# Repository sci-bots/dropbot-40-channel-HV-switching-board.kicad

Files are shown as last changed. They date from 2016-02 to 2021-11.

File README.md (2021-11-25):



# DropBot v3 40-channel high-voltage switching board

The high-voltage switching boards control the on/off state of electrodes in the [DropBot system][dropbot]. Each board controls 40-channels and multiple boards can be daisy-chained together.

For more information, please visit https://sci-bots.com

[Sci-Bots logo][sci-bots]

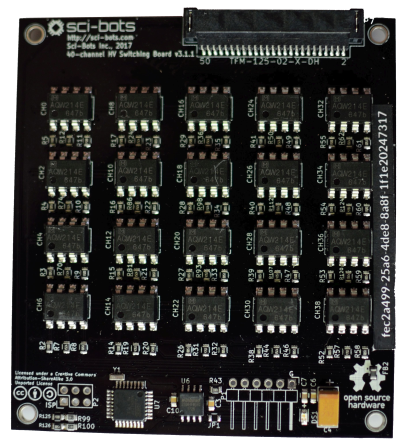
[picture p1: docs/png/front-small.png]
front

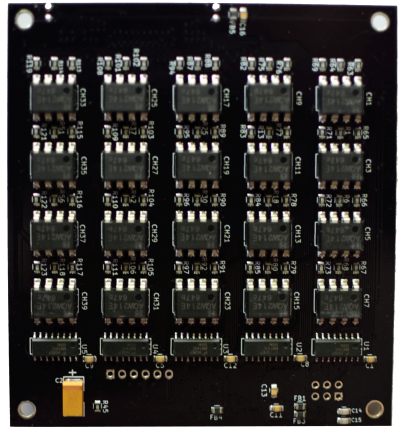
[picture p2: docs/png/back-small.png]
back


This design is open-source hardware released under a [Creative Commons Attribution-ShareAlike licence][cc-by-sa].

[][cc-by-sa]

[dropbot]: https://github.com/sci-bots/dropbot-v3
[sci-bots]: https://sci-bots.com/
[cc-by-sa]: http://creativecommons.org/licenses/by-sa/3.0

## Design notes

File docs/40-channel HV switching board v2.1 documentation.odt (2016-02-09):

40-channel HV switching board v2.1

http://microfluidics.utoronto.ca/trac/dropbot/wiki/HighVoltageSwitchingBoard

Document revision: 1

Last updated: 2016-02-09

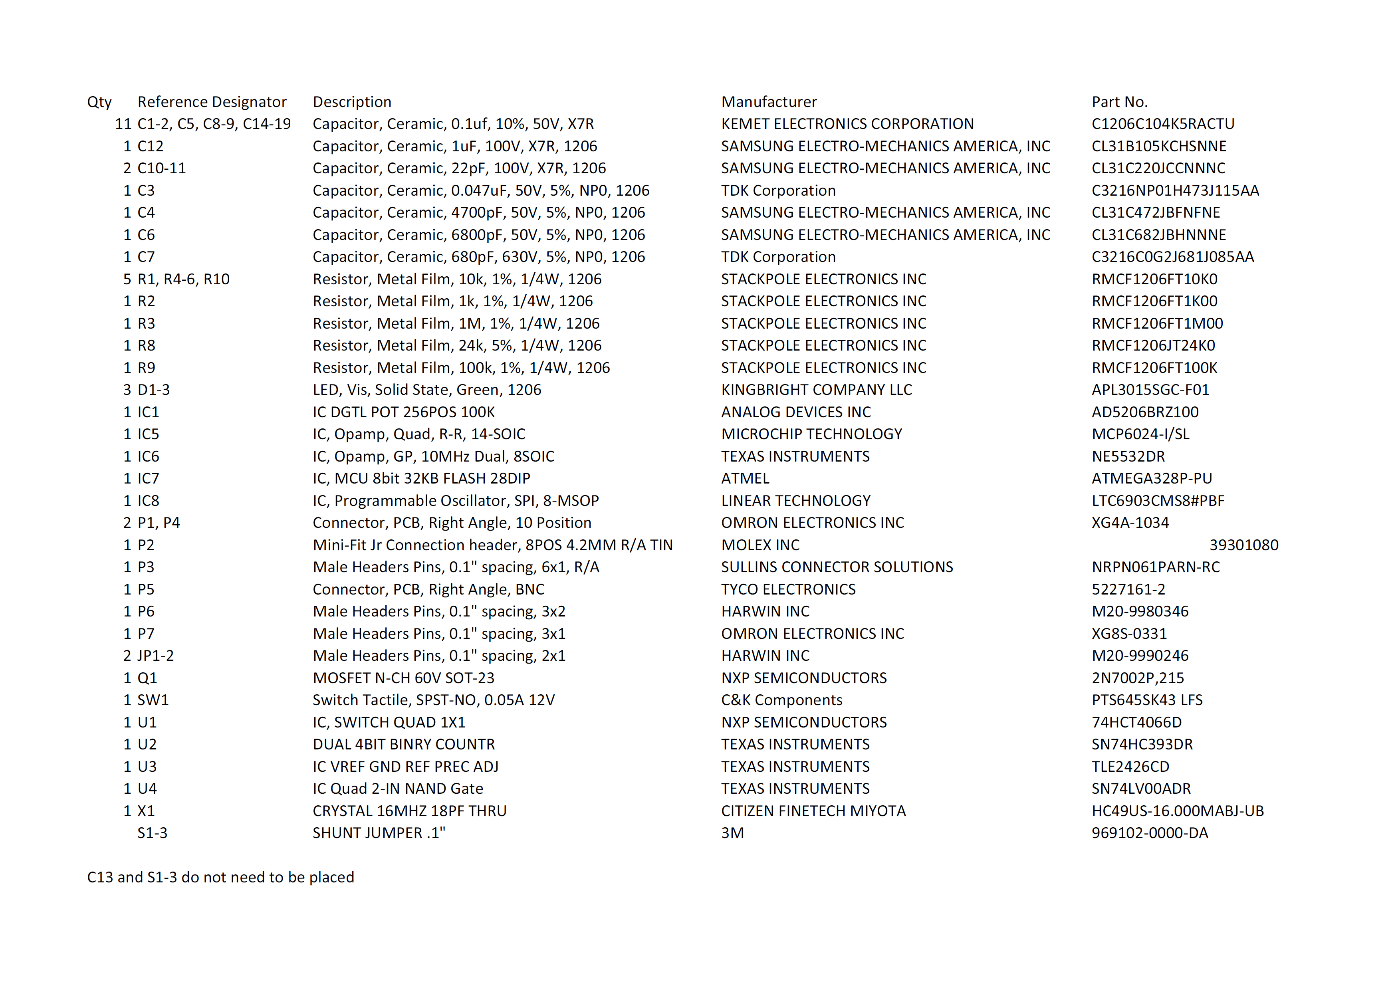
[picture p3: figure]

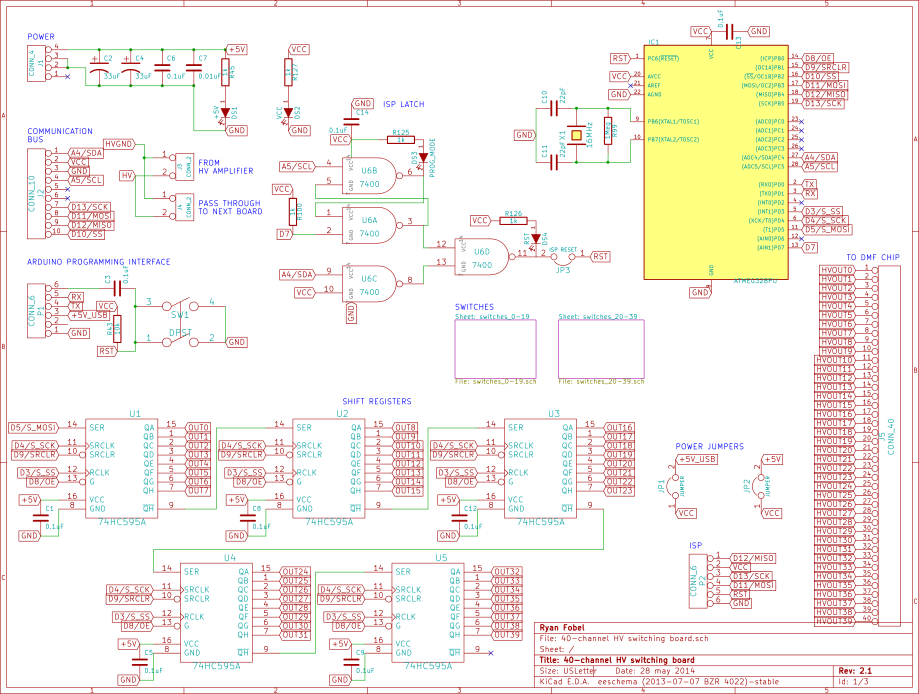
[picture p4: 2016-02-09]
docs/png/40-channel HV switching board schematic p1.png

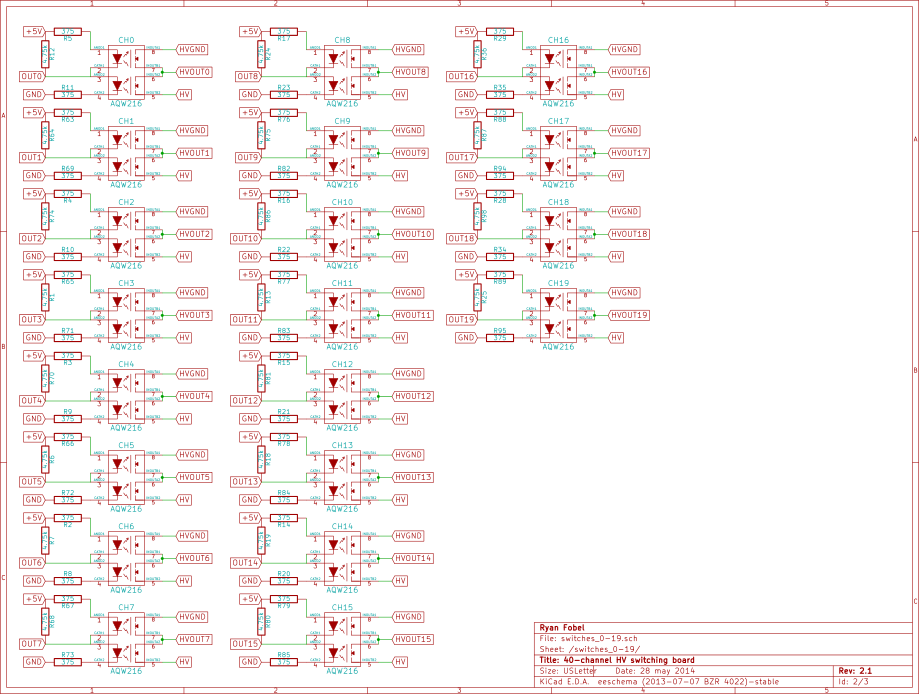
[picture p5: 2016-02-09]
docs/png/40-channel HV switching board schematic p2.png

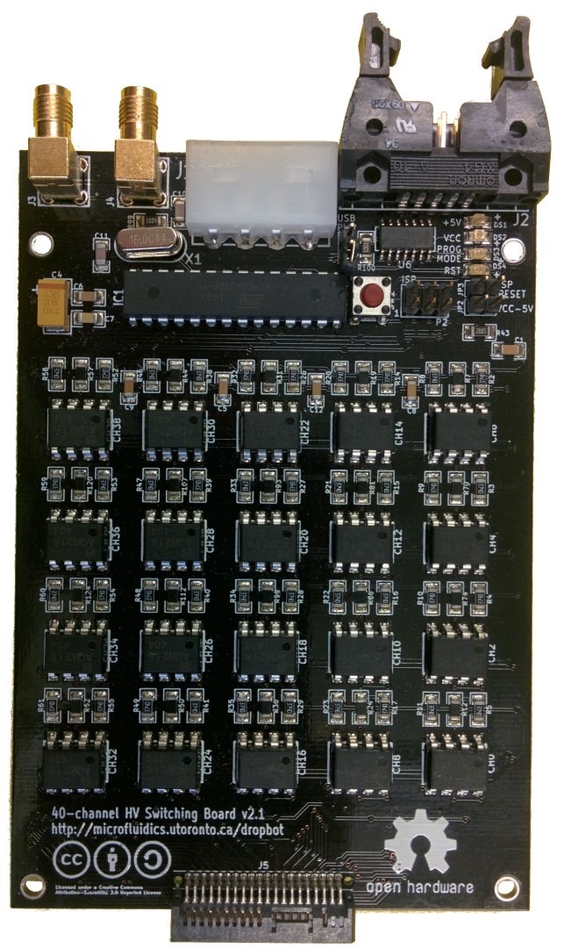
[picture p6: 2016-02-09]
docs/src/HV_Switching_Board_v2.1(front).jpg

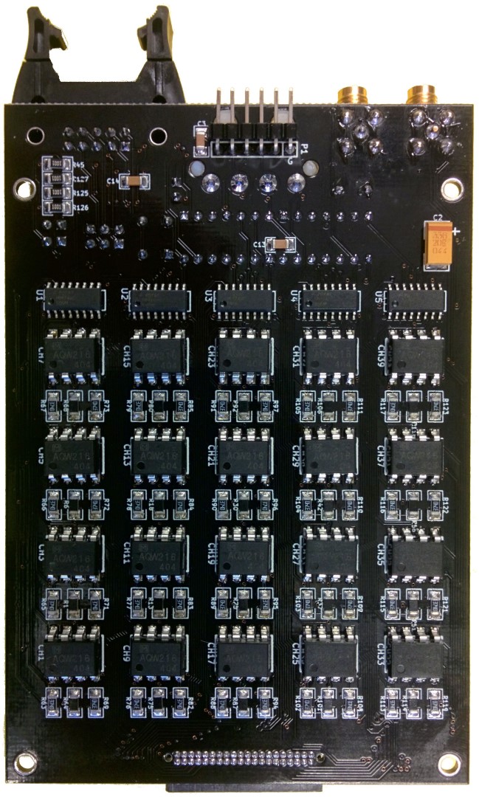
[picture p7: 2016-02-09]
docs/src/HV_Switching_Board_v2.1(back).jpg

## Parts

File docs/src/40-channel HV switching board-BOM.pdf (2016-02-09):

Item # | Qty Reference Designator | Description | Package Manufacturer | Part No. | Digikey Part No.
1 | 2 C10 C11 | Capacitor, Ceramic, 22pF, 100V, X7R, 1206 | 1206 SAMSUNG ELECTRO-MECHANICS AMERICA, INC | CL31C220JCCNNNC | 1276-2820-1-ND
2 | 1 C7 | Capacitor, Ceramic, 0.01uf, 10%, 50V, X7R | 1206 SAMSUNG ELECTRO-MECHANICS AMERICA, INC | CL31B103KBCNNNC | 1276-1035-1-ND
3 | 9 C1 C3 C5 C6 C8 C9 C12 C13 C14 | Capacitor, Ceramic, 0.1uf, 10%, 50V, X7R | 1206 KEMET ELECTRONICS CORPORATION | C1206C104K5RACTU | 399-1249-1-ND
4 | 2 C2 C4 | Capacitor, Tantalum, 33uf, 10%, 20V | 1206 KEMET ELECTRONICS CORPORATION | T491D336K020AT | 399-3788-1-ND

5 40

CH0 CH1 CH2 CH3 CH4 CH5 CH6 CH7 CH8 CH9
CH10 CH11 CH12 CH13 CH14 CH15 CH16 CH17
CH18 CH19 CH20 CH21 CH22 CH23 CH24 CH25
CH26 CH27 CH28 CH29 CH30 CH31 CH32 CH33
| CH34 CH35 CH36 CH37 CH38 CH39 | Relay, PhotoMOS, 600V | 8-SMD | Panasonic Electric Works | AQW216A | 255-1969-ND
6 | 4 DS1 DS2 DS3 DS4 | LED, Vis, Solid State, Green | 1206 KINGBRIGHT COMPANY LLC | APL3015SGC-F01 | 754-1111-1-ND
7 | 1 IC1 | IC, MCU 8bit 32KB FLASH 28DIP | 28DIP | ATMEL | ATMEGA328P-PU | ATMEGA328P-PU-ND
8 | 1 J1 | Connnection Header, 4 Position, .200, RT ANG | header | Molex Inc | 15-24-4441 | WM6988-ND
9 | 1 J2 | Connector, PCB, Right Angle, 10 Position | header | OMRON ELECTRONICS INC | XG4A-1034 | OR1001-ND
10 | 2 J3 J4 | Connector, PCB, Right Angle, SMA | header | TE CONNECTIVITY | 5-1814400-1 | A97593-ND
11 | 1 J5 | Connector, 0.05", Right Angle Header, 40 Position | header | Samtec Inc | TFML-120-01-S-D-RA | SAM8266-ND
12 | 3 JP1 JP2 JP3 | Male Headers Pins, 0.1" spacing, 2x1 | header | Harwin Inc | M20-9990246 | 952-2121-ND
13 | 1 P1 | Male Headers Pins, 0.1" spacing, 6x1, R/A | header | SULLINS CONNECTOR SOLUTIONS | PRPC006SBAN-M71RC | S1111EC-06-ND
14 | 1 P2 | Male Headers Pins, 0.1" spacing, 3x2 | header | HARWIN INC | M20-9980346 | 952-2121-ND

15 80

R2 R3 R4 R5 R8 R9 R10 R11 R14 R15 R16 R17
R20 R21 R22 R23 R26 R27 R28 R29 R32 R33 R34
R35 R38 R39 R40 R41 R46 R47 R48 R49 R52 R53 R54 R55 R58 R59 R60 R61 R63 R65 R66 R67 R69 R71 R72 R73 R76 R77 R78 R79 R82 R83 R84 R85
R88 R89 R90 R91 R94 R95 R96 R97 R102 R103
R104 R105 R108 R109 R110 R111 R113 R115
| R116 R117 R119 R121 R122 R123 | Resistor, Metal Film, 374, 1%, 1/4W | 1206 Yageo | RC1206FR-07374RL | 311-374FRCT-ND
16 | 4 R45 R100 R125 R126 R127 | Resistor, Metal Film, 1k, 1%, 1/4W, 1206 | 1206 STACKPOLE ELECTRONICS INC | RMCF1206FT1K00 | RMCF1206FT1K00CT-ND

17 40

R1 R6 R7 R12 R13 R18 R19 R24 R25 R30 R31
R36 R37 R42 R44 R50 R51 R56 R57 R62 R64 R68
R70 R74 R75 R80 R81 R86 R87 R92 R93 R98
R101 R106 R107 R112 R114 R118 R120 R124 | Resistor, Metal Film, 4.75k, 1%, 1/8W | 1206 Yageo | RC1206FR-074K75L | 311-4.75KFRCT-ND
18 | 1 R43 | Resistor, Metal Film, 10k, 1%, 1/4W, 1206 | 1206 STACKPOLE ELECTRONICS INC | RMCF1206FT10K0 | RMCF1206FT10K0TR-ND
19 | 1 R99 | Resistor, Metal Film, 1M, 1%, 1/4W, 1206 | 1206 STACKPOLE ELECTRONICS INC | RMCF1206FT1M00 | RMCF1206FT1M00TR-ND
20 | 3 S1 S2 S3 | Shunt Jumper .1" | N/A | 3M | 969102-0000-DA | 3M9580-ND
21 | 1 SW1 | Switch Tactile, SPST-NO, 0.05A 12V | button | C&K Components | PTS645SK43 LFS | CKN9090-ND
22 | 1 U6 | IC Quad 2-IN NAND Gate | 14-SOIC Texas Instruments | SN74LV00ADR | 296-1670-1-ND
23 | 5 U1 U2 U3 U4 U5 | IC Shift Register 8-BIT | 16-SOIC Fairchild Semiconductor | MM74HC595MX | MM74HC595MXCT-ND
24 | 1 X1 | Crytal 16MHZ 18pF | HC49/US CITIZEN FINETECH MIYOTA | HC49US-16.000MABJ-UB 300-8499-ND

Note: S1-3 do not need to be placed

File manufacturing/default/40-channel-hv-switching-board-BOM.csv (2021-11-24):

Refs | Quantity | MPN | Manufacturer | datasheet | footprint | value
C1, C3, C5, C6, C8-C13, C16 | 11 | CL21B104KBCNNNC | Samsung |  | Capacitors_SMD:C_0805 | 0.1uF
C14, C15 | 2 | CL21C151JBANNNC | Samsung |  | Capacitors_SMD:C_0805 | 150pF
C2, C4 | 2 | T491D336K020AT | KEMET |  | Sci-Bots:SM2917 | 33uF
C7 | 1 | CL21B103KCANNNC | Samsung |  | Capacitors_SMD:C_0805 | 0.01uF
DS1 | 1 | 150080BS75000 | Würth Elektronik |  | LEDs:LED_0805 | +3.3V_PWR
FB1-FB5 | 5 | 742792040 | Würth Elektronik |  | Resistors_SMD:R_0805 | FERRITE
JP1 | 1 | DNP | DNP |  | Resistors_SMD:R_0805 | JUMPER
P1 | 1 | DNP | DNP |  | Pin_Headers:Pin_Header_Angled_1x06 | CONN_01X06
P2 | 1 | DNP | DNP |  | Pin_Headers:Pin_Header_Straight_2x03 | CONN_01X06
P3-P6 | 4 | DNP | DNP |  | Connect:1pin | CONN_01X01
P7 | 1 | TFM-125-02-L-DH | Samtec |  | Sci-Bots:TFM-125-02-X-DH | TFM-125-02-X-DH
R99, R100 | 2 | RC0805FR-0751RL | Yageo |  | Resistors_SMD:R_0805 | 51
R125, R126 | 2 | RC0805FR-07150RL | Yageo |  | Resistors_SMD:R_0805 | 150
R43 | 1 | RC0805FR-0710KL | Yageo |  | Resistors_SMD:R_0805 | 10k
R45 | 1 | RC0805FR-071KL | Yageo |  | Resistors_SMD:R_0805 | 1k
U1-U5 | 5 | MM74HC595MX | onsemi | ~ | Sci-Bots:SO16E | 74HC595A
U6 | 1 | W25Q64FVSSIG TR | Winbond |  | SMD_Packages:SOIC-8-N | W25Q64FV
U7 | 1 | ATMEGA328P-AU | Microchip |  | Housings_QFP:TQFP-32_7x7mm_Pitch0.8mm | ATMEGA328P-AU
Y1 | 1 | CSTCE8M00G55-R0 | Murata | http://www.murata.com/~/media/webrenewal/support/library/catalog/products/timingdevice/ceralock/p16e.ashx | Sci-Bots:CSTCE_G15C | RESONATOR
CH0-CH39 | 40 | AQW214EAZ | Panasonic |  | SMD_Packages:DIP-8_SMD | AQW214
R1, R6, R7, R12, R13, R18, R19, R24, R25, R30, R31, R36, R37, R42, R44, R50, R51, R56, R57, R62, R64, R68, R70, R74, R75, R80, R81, R86, R87, R92, R93, R98, R101, R106, R107, R112, R114, R118, R120, R124 | 40 | RC0805FR-074K75L | Yageo |  | Resistors_SMD:R_0805 | 4.75k
R2-R5, R8-R11, R14-R17, R20-R23, R26-R29, R32-R35, R38-R41, R46-R49, R52-R55, R58-R61, R63, R65-R67, R69, R71-R73, R76-R79, R82-R85, R88-R91, R94-R97, R102-R105, R108-R111, R113, R115-R117, R119, R121-R123 | 80 | RC0805FR-07220RL | Yageo |  | Resistors_SMD:R_0805 | 220

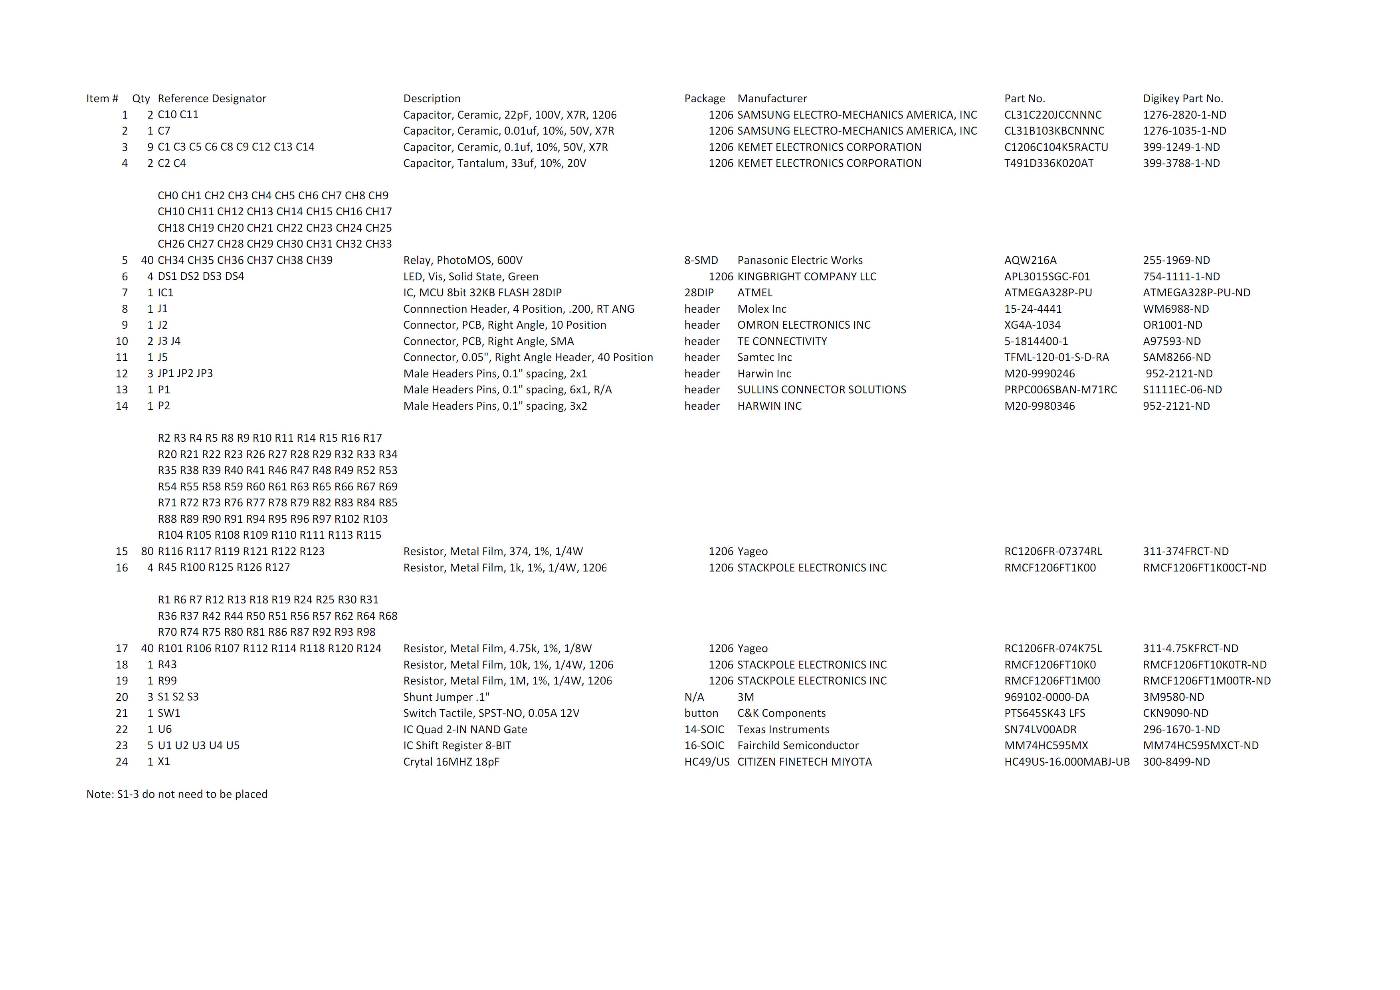
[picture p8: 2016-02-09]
docs/png/40-channel HV switching board-BOM.png

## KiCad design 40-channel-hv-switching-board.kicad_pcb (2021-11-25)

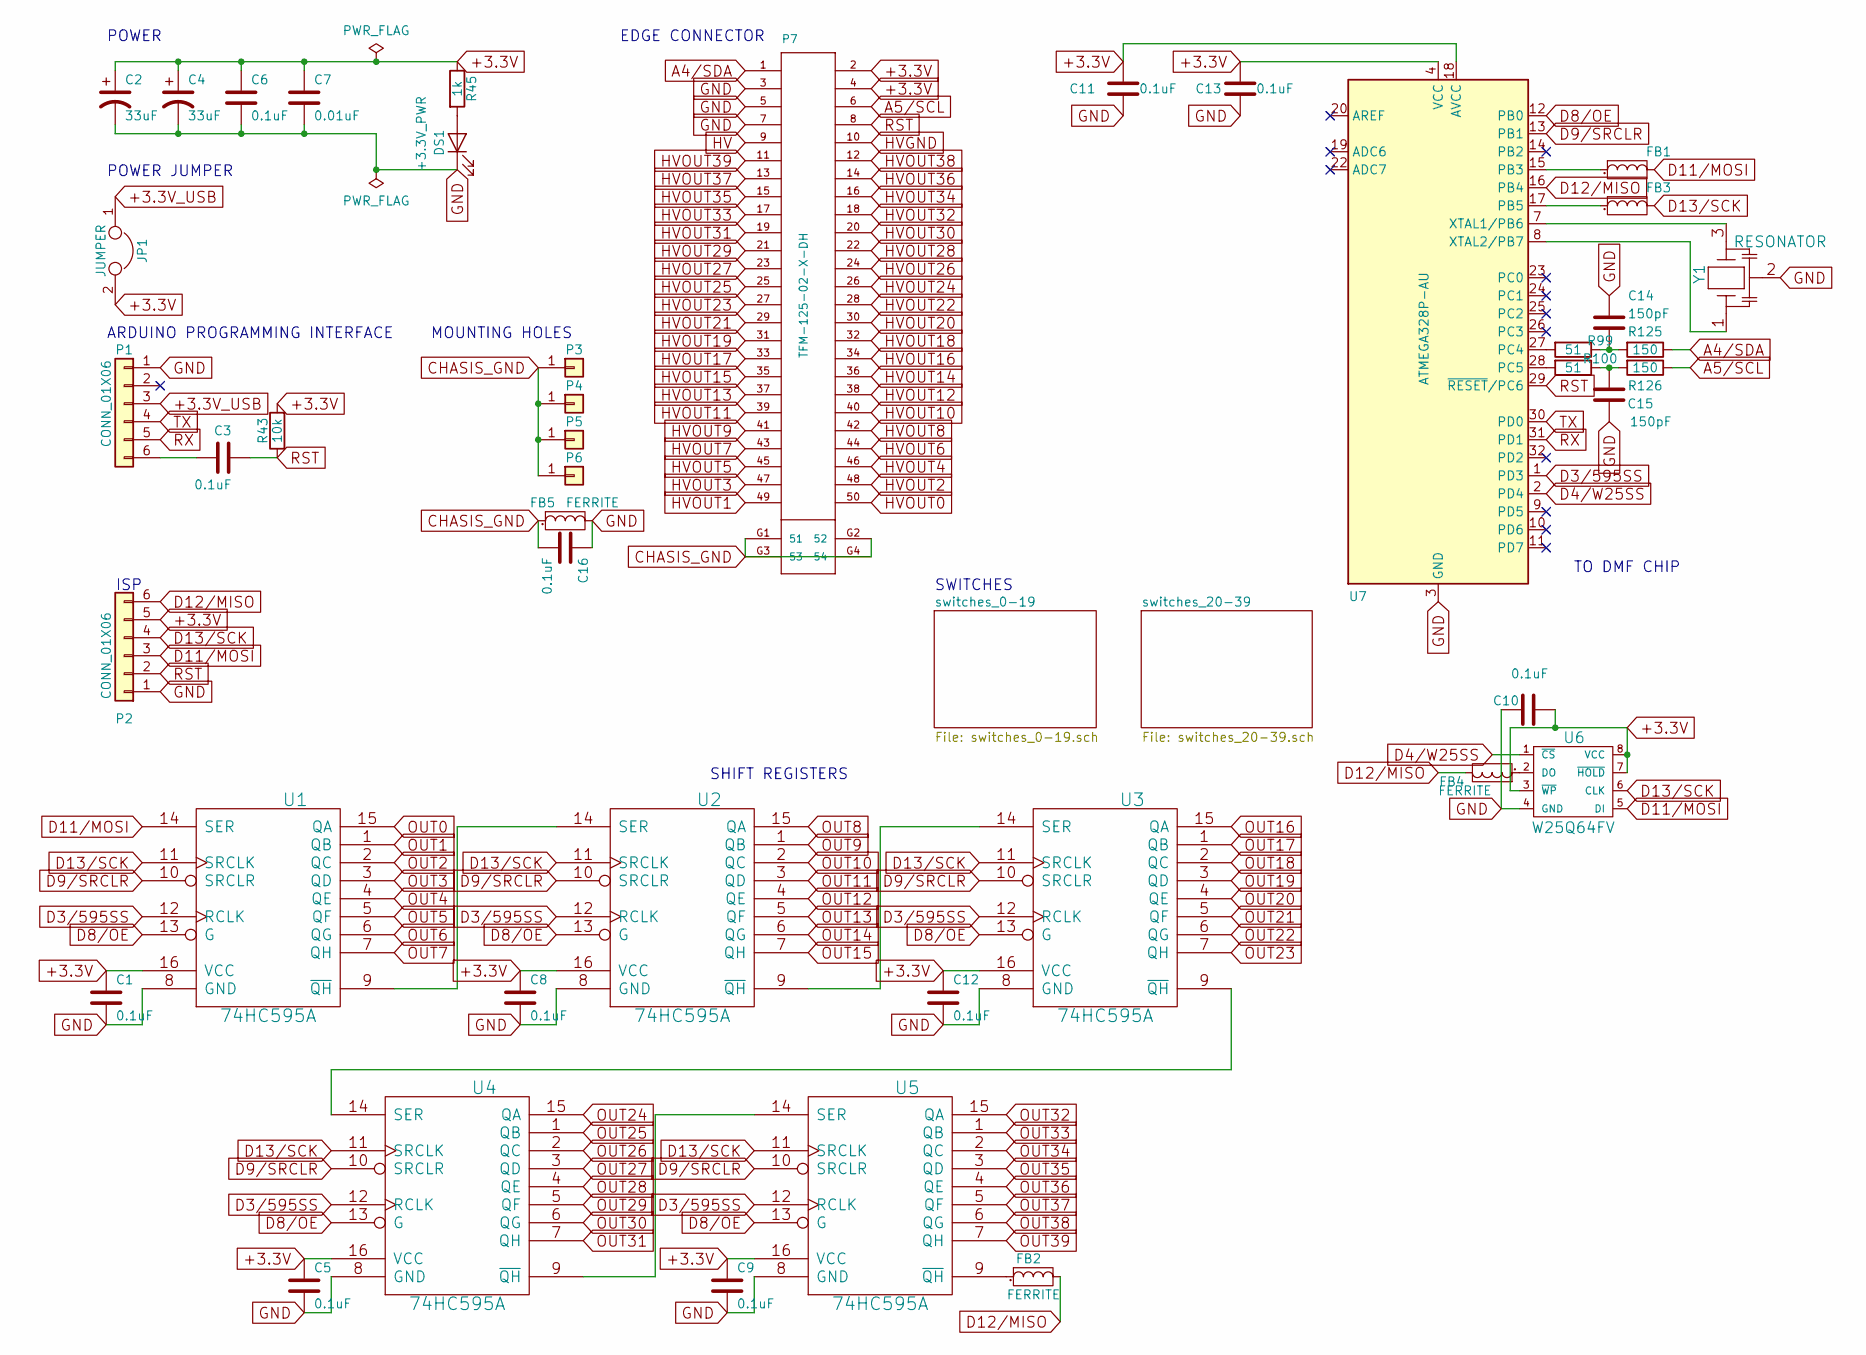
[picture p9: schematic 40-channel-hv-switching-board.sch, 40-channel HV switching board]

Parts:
C1, C3, C5, C6, C8, C9, C10, C11, C12, C13, C16: 0.1uF; C_0805; MPN CL21B104KBCNNNC
C2, C4: 33uF; SM2917; MPN T491D336K020AT
C7: 0.01uF; C_0805; MPN CL21B103KCANNNC
C14, C15: 150pF; C_0805; MPN CL21C151JBANNNC
DS1: +3.3V_PWR; LED_0805; MPN 150080BS75000
FB1, FB2, FB3, FB4, FB5: FERRITE; R_0805; MPN 742792040
JP1: JUMPER; R_0805; MPN DNP
P1: CONN_01X06; Pin_Header_Angled_1x06; MPN DNP
P2: CONN_01X06; Pin_Header_Straight_2x03; MPN DNP
P3, P4, P5, P6: CONN_01X01; 1pin; MPN DNP
P7: TFM-125-02-X-DH; MPN TFM-125-02-L-DH
R43: 10k; R_0805; MPN RC0805FR-0710KL
R45: 1k; R_0805; MPN RC0805FR-071KL
R99, R100: 51; R_0805; MPN RC0805FR-0751RL
R125, R126: 150; R_0805; MPN RC0805FR-07150RL
U1, U2, U3, U4, U5: 74HC595A; SO16E; MPN MM74HC595MX
U6: W25Q64FV; SOIC-8-N; MPN W25Q64FVSSIG TR
U7: ATMEGA328P-AU; TQFP-32_7x7mm_Pitch0.8mm; MPN ATMEGA328P-AU
Y1: RESONATOR; CSTCE_G15C; MPN CSTCE8M00G55-R0

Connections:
+3.3V: C1.1, C2.1, C4.1, C5.1, C6.1, C7.1, C8.1, C9.1, C10.1, C11.2, C12.1, C13.2, JP1.2, P2.5, P7.2, P7.4, R43.2, R45.1, U1.16 (VCC), U2.16 (VCC), U3.16 (VCC), U4.16 (VCC), U5.16 (VCC), U6.3 (~WP), U6.7 (~HOLD), U6.8 (VCC), U7.4 (VCC), U7.6 (VCC), U7.18 (AVCC); also elsewhere on the board
+3.3V_USB: JP1.1, P1.3
A4/SDA: P7.1, R125.1
A5/SCL: P7.6, R126.1
CHASIS_GND: C16.2, FB5.1, P3.1, P4.1, P5.1, P6.1, P7.G1 (51), P7.G2 (52), P7.G3 (53), P7.G4 (54)
D3/595SS: U1.12 (RCLK), U2.12 (RCLK), U3.12 (RCLK), U4.12 (RCLK), U5.12 (RCLK), U7.1 (PD3)
D4/W25SS: U6.1 (~CS), U7.2 (PD4)
D8/OE: U1.13 (G), U2.13 (G), U3.13 (G), U4.13 (G), U5.13 (G), U7.12 (PB0)
D9/SRCLR: U1.10 (SRCLR), U2.10 (SRCLR), U3.10 (SRCLR), U4.10 (SRCLR), U5.10 (SRCLR), U7.13 (PB1)
D11/MOSI: FB1.2, P2.3, U1.14 (SER), U6.5 (DI)
D12/MISO: FB2.2, FB4.2, P2.6, U7.16 (PB4)
D13/SCK: FB3.2, P2.4, U1.11 (SRCLK), U2.11 (SRCLK), U3.11 (SRCLK), U4.11 (SRCLK), U5.11 (SRCLK), U6.6 (CLK)
GND: C1.2, C2.2, C4.2, C5.2, C6.2, C7.2, C8.2, C9.2, C10.2, C11.1, C12.2, C13.1, C14.1, C15.1, C16.1, DS1.1 (K), FB5.2, P1.1, P2.1, P7.3, P7.5, P7.7, U1.8 (GND), U2.8 (GND), U3.8 (GND), U4.8 (GND), U5.8 (GND), U6.4 (GND), U7.3 (GND), U7.5 (GND), U7.21 (GND), Y1.2; also elsewhere on the board
HV: P7.9; also elsewhere on the board
HVGND: P7.10; also elsewhere on the board
HVOUT0: P7.50; also elsewhere on the board
HVOUT1: P7.49; also elsewhere on the board
HVOUT2: P7.48; also elsewhere on the board
HVOUT3: P7.47; also elsewhere on the board
HVOUT4: P7.46; also elsewhere on the board
HVOUT5: P7.45; also elsewhere on the board
HVOUT6: P7.44; also elsewhere on the board
HVOUT7: P7.43; also elsewhere on the board
HVOUT8: P7.42; also elsewhere on the board
HVOUT9: P7.41; also elsewhere on the board
HVOUT10: P7.40; also elsewhere on the board
HVOUT11: P7.39; also elsewhere on the board
HVOUT12: P7.38; also elsewhere on the board
HVOUT13: P7.37; also elsewhere on the board
HVOUT14: P7.36; also elsewhere on the board
HVOUT15: P7.35; also elsewhere on the board
HVOUT16: P7.34; also elsewhere on the board
HVOUT17: P7.33; also elsewhere on the board
HVOUT18: P7.32; also elsewhere on the board
HVOUT19: P7.31; also elsewhere on the board
HVOUT20: P7.30; also elsewhere on the board
HVOUT21: P7.29; also elsewhere on the board
HVOUT22: P7.28; also elsewhere on the board
HVOUT23: P7.27; also elsewhere on the board
HVOUT24: P7.26; also elsewhere on the board
HVOUT25: P7.25; also elsewhere on the board
HVOUT26: P7.24; also elsewhere on the board
HVOUT27: P7.23; also elsewhere on the board
HVOUT28: P7.22; also elsewhere on the board
HVOUT29: P7.21; also elsewhere on the board
HVOUT30: P7.20; also elsewhere on the board
HVOUT31: P7.19; also elsewhere on the board
HVOUT32: P7.18; also elsewhere on the board
HVOUT33: P7.17; also elsewhere on the board
HVOUT34: P7.16; also elsewhere on the board
HVOUT35: P7.15; also elsewhere on the board
HVOUT36: P7.14; also elsewhere on the board
HVOUT37: P7.13; also elsewhere on the board
HVOUT38: P7.12; also elsewhere on the board
HVOUT39: P7.11; also elsewhere on the board
unnamed: C3.1, P1.6
unnamed: C14.2, R99.1, R125.2
unnamed: C15.2, R100.1, R126.2
unnamed: DS1.2 (A), R45.2
unnamed: FB1.1, U7.15 (PB3)
unnamed: FB2.1, U5.9 (~QH)
unnamed: FB3.1, U7.17 (PB5)
unnamed: FB4.1, U6.2 (DO)
unnamed: R99.2, U7.27 (PC4)
unnamed: R100.2, U7.28 (PC5)
unnamed: U1.9 (~QH), U2.14 (SER)
unnamed: U2.9 (~QH), U3.14 (SER)
unnamed: U3.9 (~QH), U4.14 (SER)
unnamed: U4.9 (~QH), U5.14 (SER)
unnamed: U7.7 (XTAL1/PB6), Y1.3
unnamed: U7.8 (XTAL2/PB7), Y1.1
OUT0: U1.15 (QA); also elsewhere on the board
OUT1: U1.1 (QB); also elsewhere on the board
OUT2: U1.2 (QC); also elsewhere on the board
OUT3: U1.3 (QD); also elsewhere on the board
OUT4: U1.4 (QE); also elsewhere on the board
OUT5: U1.5 (QF); also elsewhere on the board
OUT6: U1.6 (QG); also elsewhere on the board
OUT7: U1.7 (QH); also elsewhere on the board
OUT8: U2.15 (QA); also elsewhere on the board
OUT9: U2.1 (QB); also elsewhere on the board
OUT10: U2.2 (QC); also elsewhere on the board
OUT11: U2.3 (QD); also elsewhere on the board
OUT12: U2.4 (QE); also elsewhere on the board
OUT13: U2.5 (QF); also elsewhere on the board
OUT14: U2.6 (QG); also elsewhere on the board
OUT15: U2.7 (QH); also elsewhere on the board
OUT16: U3.15 (QA); also elsewhere on the board
OUT17: U3.1 (QB); also elsewhere on the board
OUT18: U3.2 (QC); also elsewhere on the board
OUT19: U3.3 (QD); also elsewhere on the board
OUT20: U3.4 (QE); also elsewhere on the board
OUT21: U3.5 (QF); also elsewhere on the board
OUT22: U3.6 (QG); also elsewhere on the board
OUT23: U3.7 (QH); also elsewhere on the board
OUT24: U4.15 (QA); also elsewhere on the board
OUT25: U4.1 (QB); also elsewhere on the board
OUT26: U4.2 (QC); also elsewhere on the board
OUT27: U4.3 (QD); also elsewhere on the board
OUT28: U4.4 (QE); also elsewhere on the board
OUT29: U4.5 (QF); also elsewhere on the board
OUT30: U4.6 (QG); also elsewhere on the board
OUT31: U4.7 (QH); also elsewhere on the board
OUT32: U5.15 (QA); also elsewhere on the board
OUT33: U5.1 (QB); also elsewhere on the board
OUT34: U5.2 (QC); also elsewhere on the board
OUT35: U5.3 (QD); also elsewhere on the board
OUT36: U5.4 (QE); also elsewhere on the board
OUT37: U5.5 (QF); also elsewhere on the board
OUT38: U5.6 (QG); also elsewhere on the board
OUT39: U5.7 (QH); also elsewhere on the board
RST: C3.2, P2.2, P7.8, R43.1, U7.29 (~RESET~/PC6)
RX: P1.5, U7.31 (PD1)
TX: P1.4, U7.30 (PD0)

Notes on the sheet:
SHIFT REGISTERS
TO DMF CHIP
POWER
ARDUINO PROGRAMMING INTERFACE
ISP
POWER JUMPER
SWITCHES
EDGE CONNECTOR
MOUNTING HOLES

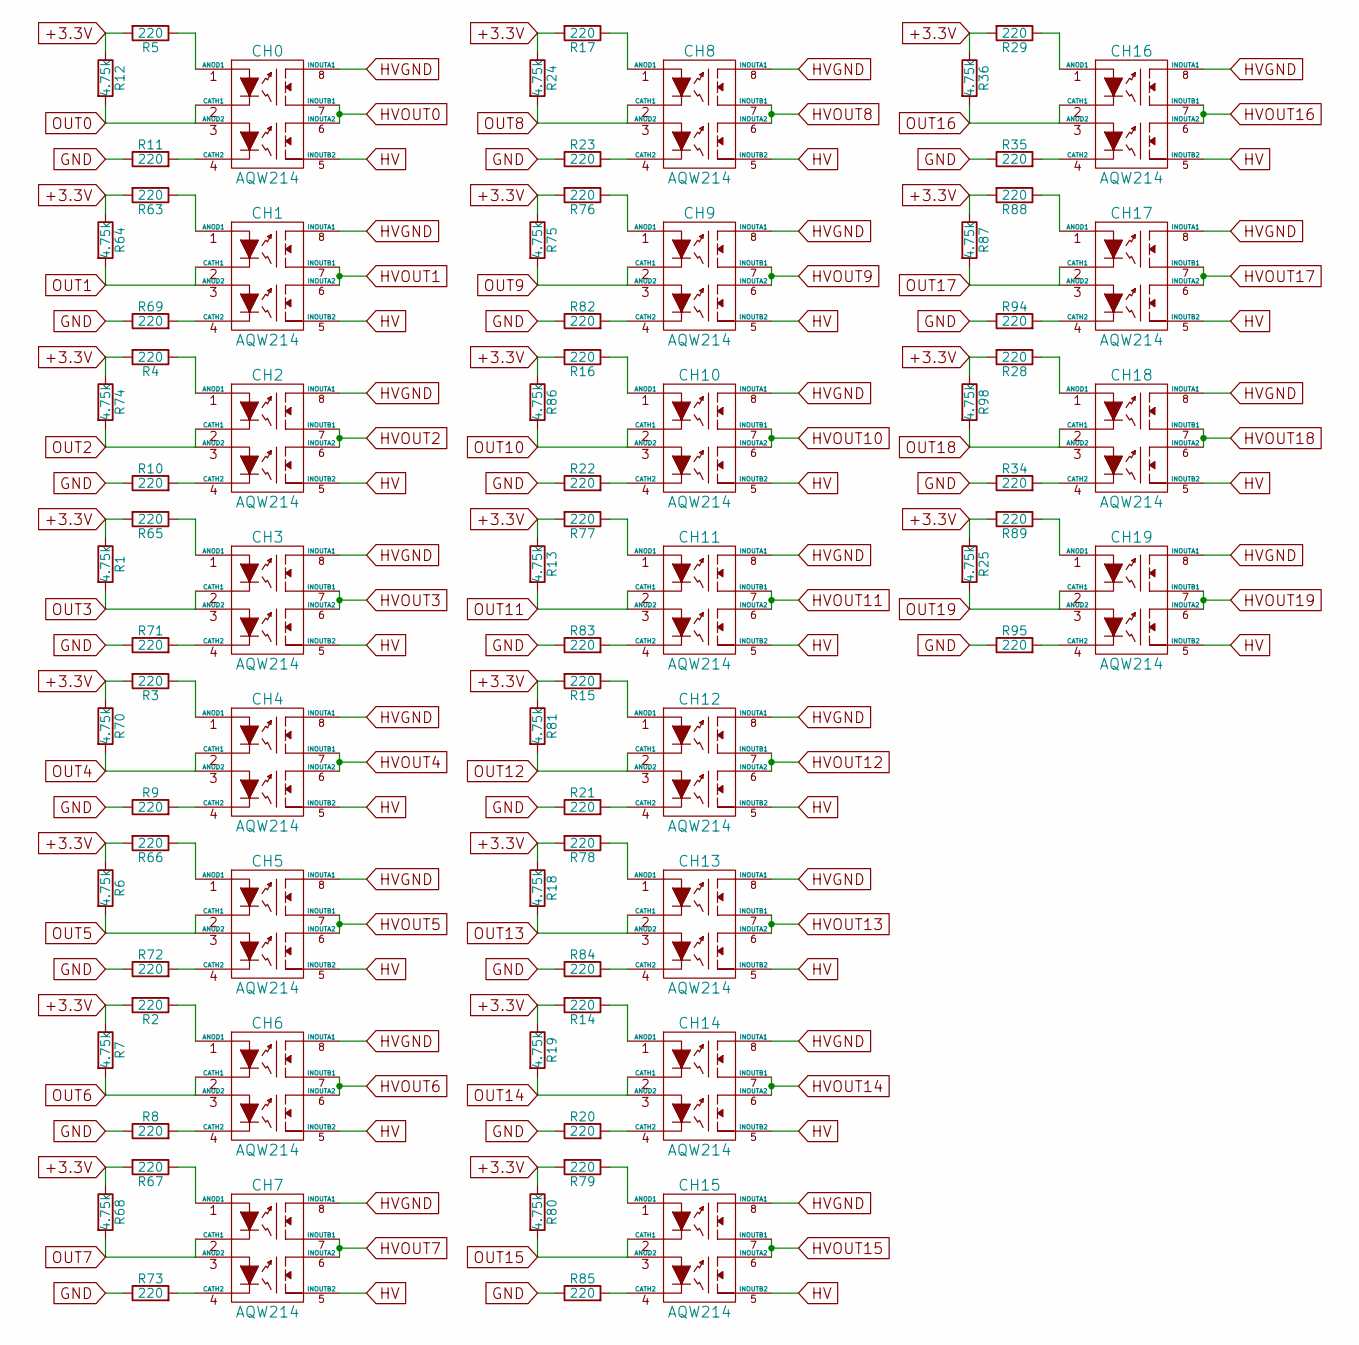
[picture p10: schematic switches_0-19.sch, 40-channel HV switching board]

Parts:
CH0, CH1, CH2, CH3, CH4, CH5, CH6, CH7, CH8, CH9, CH10, CH11, CH12, CH13, CH14, CH15, CH16, CH17, CH18, CH19: AQW214; DIP-8_SMD; MPN AQW214EAZ
R1, R6, R7, R12, R13, R18, R19, R24, R25, R36, R64, R68, R70, R74, R75, R80, R81, R86, R87, R98: 4.75k; R_0805; MPN RC0805FR-074K75L
R2, R3, R4, R5, R8, R9, R10, R11, R14, R15, R16, R17, R20, R21, R22, R23, R28, R29, R34, R35, R63, R65, R66, R67, R69, R71, R72, R73, R76, R77, R78, R79, R82, R83, R84, R85, R88, R89, R94, R95: 220; R_0805; MPN RC0805FR-07220RL

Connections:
+3.3V: R1.1, R2.2, R3.2, R4.2, R5.2, R6.1, R7.1, R12.1, R13.1, R14.2, R15.2, R16.2, R17.2, R18.1, R19.1, R24.1, R25.1, R28.2, R29.2, R36.1, R63.2, R64.1, R65.2, R66.2, R67.2, R68.1, R70.1, R74.1, R75.1, R76.2, R77.2, R78.2, R79.2, R80.1, R81.1, R86.1, R87.1, R88.2, R89.2, R98.1; also elsewhere on the board
GND: R8.1, R9.1, R10.1, R11.1, R20.1, R21.1, R22.1, R23.1, R34.1, R35.1, R69.1, R71.1, R72.1, R73.1, R82.1, R83.1, R84.1, R85.1, R94.1, R95.1; also elsewhere on the board
HV: CH0.5 (INOUTB2), CH1.5 (INOUTB2), CH2.5 (INOUTB2), CH3.5 (INOUTB2), CH4.5 (INOUTB2), CH5.5 (INOUTB2), CH6.5 (INOUTB2), CH7.5 (INOUTB2), CH8.5 (INOUTB2), CH9.5 (INOUTB2), CH10.5 (INOUTB2), CH11.5 (INOUTB2), CH12.5 (INOUTB2), CH13.5 (INOUTB2), CH14.5 (INOUTB2), CH15.5 (INOUTB2), CH16.5 (INOUTB2), CH17.5 (INOUTB2), CH18.5 (INOUTB2), CH19.5 (INOUTB2); also elsewhere on the board
HVGND: CH0.8 (INOUTA1), CH1.8 (INOUTA1), CH2.8 (INOUTA1), CH3.8 (INOUTA1), CH4.8 (INOUTA1), CH5.8 (INOUTA1), CH6.8 (INOUTA1), CH7.8 (INOUTA1), CH8.8 (INOUTA1), CH9.8 (INOUTA1), CH10.8 (INOUTA1), CH11.8 (INOUTA1), CH12.8 (INOUTA1), CH13.8 (INOUTA1), CH14.8 (INOUTA1), CH15.8 (INOUTA1), CH16.8 (INOUTA1), CH17.8 (INOUTA1), CH18.8 (INOUTA1), CH19.8 (INOUTA1); also elsewhere on the board
HVOUT0: CH0.6 (INOUTA2), CH0.7 (INOUTB1); also elsewhere on the board
HVOUT1: CH1.6 (INOUTA2), CH1.7 (INOUTB1); also elsewhere on the board
HVOUT2: CH2.6 (INOUTA2), CH2.7 (INOUTB1); also elsewhere on the board
HVOUT3: CH3.6 (INOUTA2), CH3.7 (INOUTB1); also elsewhere on the board
HVOUT4: CH4.6 (INOUTA2), CH4.7 (INOUTB1); also elsewhere on the board
HVOUT5: CH5.6 (INOUTA2), CH5.7 (INOUTB1); also elsewhere on the board
HVOUT6: CH6.6 (INOUTA2), CH6.7 (INOUTB1); also elsewhere on the board
HVOUT7: CH7.6 (INOUTA2), CH7.7 (INOUTB1); also elsewhere on the board
HVOUT8: CH8.6 (INOUTA2), CH8.7 (INOUTB1); also elsewhere on the board
HVOUT9: CH9.6 (INOUTA2), CH9.7 (INOUTB1); also elsewhere on the board
HVOUT10: CH10.6 (INOUTA2), CH10.7 (INOUTB1); also elsewhere on the board
HVOUT11: CH11.6 (INOUTA2), CH11.7 (INOUTB1); also elsewhere on the board
HVOUT12: CH12.6 (INOUTA2), CH12.7 (INOUTB1); also elsewhere on the board
HVOUT13: CH13.6 (INOUTA2), CH13.7 (INOUTB1); also elsewhere on the board
HVOUT14: CH14.6 (INOUTA2), CH14.7 (INOUTB1); also elsewhere on the board
HVOUT15: CH15.6 (INOUTA2), CH15.7 (INOUTB1); also elsewhere on the board
HVOUT16: CH16.6 (INOUTA2), CH16.7 (INOUTB1); also elsewhere on the board
HVOUT17: CH17.6 (INOUTA2), CH17.7 (INOUTB1); also elsewhere on the board
HVOUT18: CH18.6 (INOUTA2), CH18.7 (INOUTB1); also elsewhere on the board
HVOUT19: CH19.6 (INOUTA2), CH19.7 (INOUTB1); also elsewhere on the board
unnamed: CH0.1 (ANOD1), R5.1
unnamed: CH0.4 (CATH2), R11.2
unnamed: CH1.1 (ANOD1), R63.1
unnamed: CH1.4 (CATH2), R69.2
unnamed: CH2.1 (ANOD1), R4.1
unnamed: CH2.4 (CATH2), R10.2
unnamed: CH3.1 (ANOD1), R65.1
unnamed: CH3.4 (CATH2), R71.2
unnamed: CH4.1 (ANOD1), R3.1
unnamed: CH4.4 (CATH2), R9.2
unnamed: CH5.1 (ANOD1), R66.1
unnamed: CH5.4 (CATH2), R72.2
unnamed: CH6.1 (ANOD1), R2.1
unnamed: CH6.4 (CATH2), R8.2
unnamed: CH7.1 (ANOD1), R67.1
unnamed: CH7.4 (CATH2), R73.2
unnamed: CH8.1 (ANOD1), R17.1
unnamed: CH8.4 (CATH2), R23.2
unnamed: CH9.1 (ANOD1), R76.1
unnamed: CH9.4 (CATH2), R82.2
unnamed: CH10.1 (ANOD1), R16.1
unnamed: CH10.4 (CATH2), R22.2
unnamed: CH11.1 (ANOD1), R77.1
unnamed: CH11.4 (CATH2), R83.2
unnamed: CH12.1 (ANOD1), R15.1
unnamed: CH12.4 (CATH2), R21.2
unnamed: CH13.1 (ANOD1), R78.1
unnamed: CH13.4 (CATH2), R84.2
unnamed: CH14.1 (ANOD1), R14.1
unnamed: CH14.4 (CATH2), R20.2
unnamed: CH15.1 (ANOD1), R79.1
unnamed: CH15.4 (CATH2), R85.2
unnamed: CH16.1 (ANOD1), R29.1
unnamed: CH16.4 (CATH2), R35.2
unnamed: CH17.1 (ANOD1), R88.1
unnamed: CH17.4 (CATH2), R94.2
unnamed: CH18.1 (ANOD1), R28.1
unnamed: CH18.4 (CATH2), R34.2
unnamed: CH19.1 (ANOD1), R89.1
unnamed: CH19.4 (CATH2), R95.2
OUT0: CH0.2 (CATH1), CH0.3 (ANOD2), R12.2; also elsewhere on the board
OUT1: CH1.2 (CATH1), CH1.3 (ANOD2), R64.2; also elsewhere on the board
OUT2: CH2.2 (CATH1), CH2.3 (ANOD2), R74.2; also elsewhere on the board
OUT3: CH3.2 (CATH1), CH3.3 (ANOD2), R1.2; also elsewhere on the board
OUT4: CH4.2 (CATH1), CH4.3 (ANOD2), R70.2; also elsewhere on the board
OUT5: CH5.2 (CATH1), CH5.3 (ANOD2), R6.2; also elsewhere on the board
OUT6: CH6.2 (CATH1), CH6.3 (ANOD2), R7.2; also elsewhere on the board
OUT7: CH7.2 (CATH1), CH7.3 (ANOD2), R68.2; also elsewhere on the board
OUT8: CH8.2 (CATH1), CH8.3 (ANOD2), R24.2; also elsewhere on the board
OUT9: CH9.2 (CATH1), CH9.3 (ANOD2), R75.2; also elsewhere on the board
OUT10: CH10.2 (CATH1), CH10.3 (ANOD2), R86.2; also elsewhere on the board
OUT11: CH11.2 (CATH1), CH11.3 (ANOD2), R13.2; also elsewhere on the board
OUT12: CH12.2 (CATH1), CH12.3 (ANOD2), R81.2; also elsewhere on the board
OUT13: CH13.2 (CATH1), CH13.3 (ANOD2), R18.2; also elsewhere on the board
OUT14: CH14.2 (CATH1), CH14.3 (ANOD2), R19.2; also elsewhere on the board
OUT15: CH15.2 (CATH1), CH15.3 (ANOD2), R80.2; also elsewhere on the board
OUT16: CH16.2 (CATH1), CH16.3 (ANOD2), R36.2; also elsewhere on the board
OUT17: CH17.2 (CATH1), CH17.3 (ANOD2), R87.2; also elsewhere on the board
OUT18: CH18.2 (CATH1), CH18.3 (ANOD2), R98.2; also elsewhere on the board
OUT19: CH19.2 (CATH1), CH19.3 (ANOD2), R25.2; also elsewhere on the board

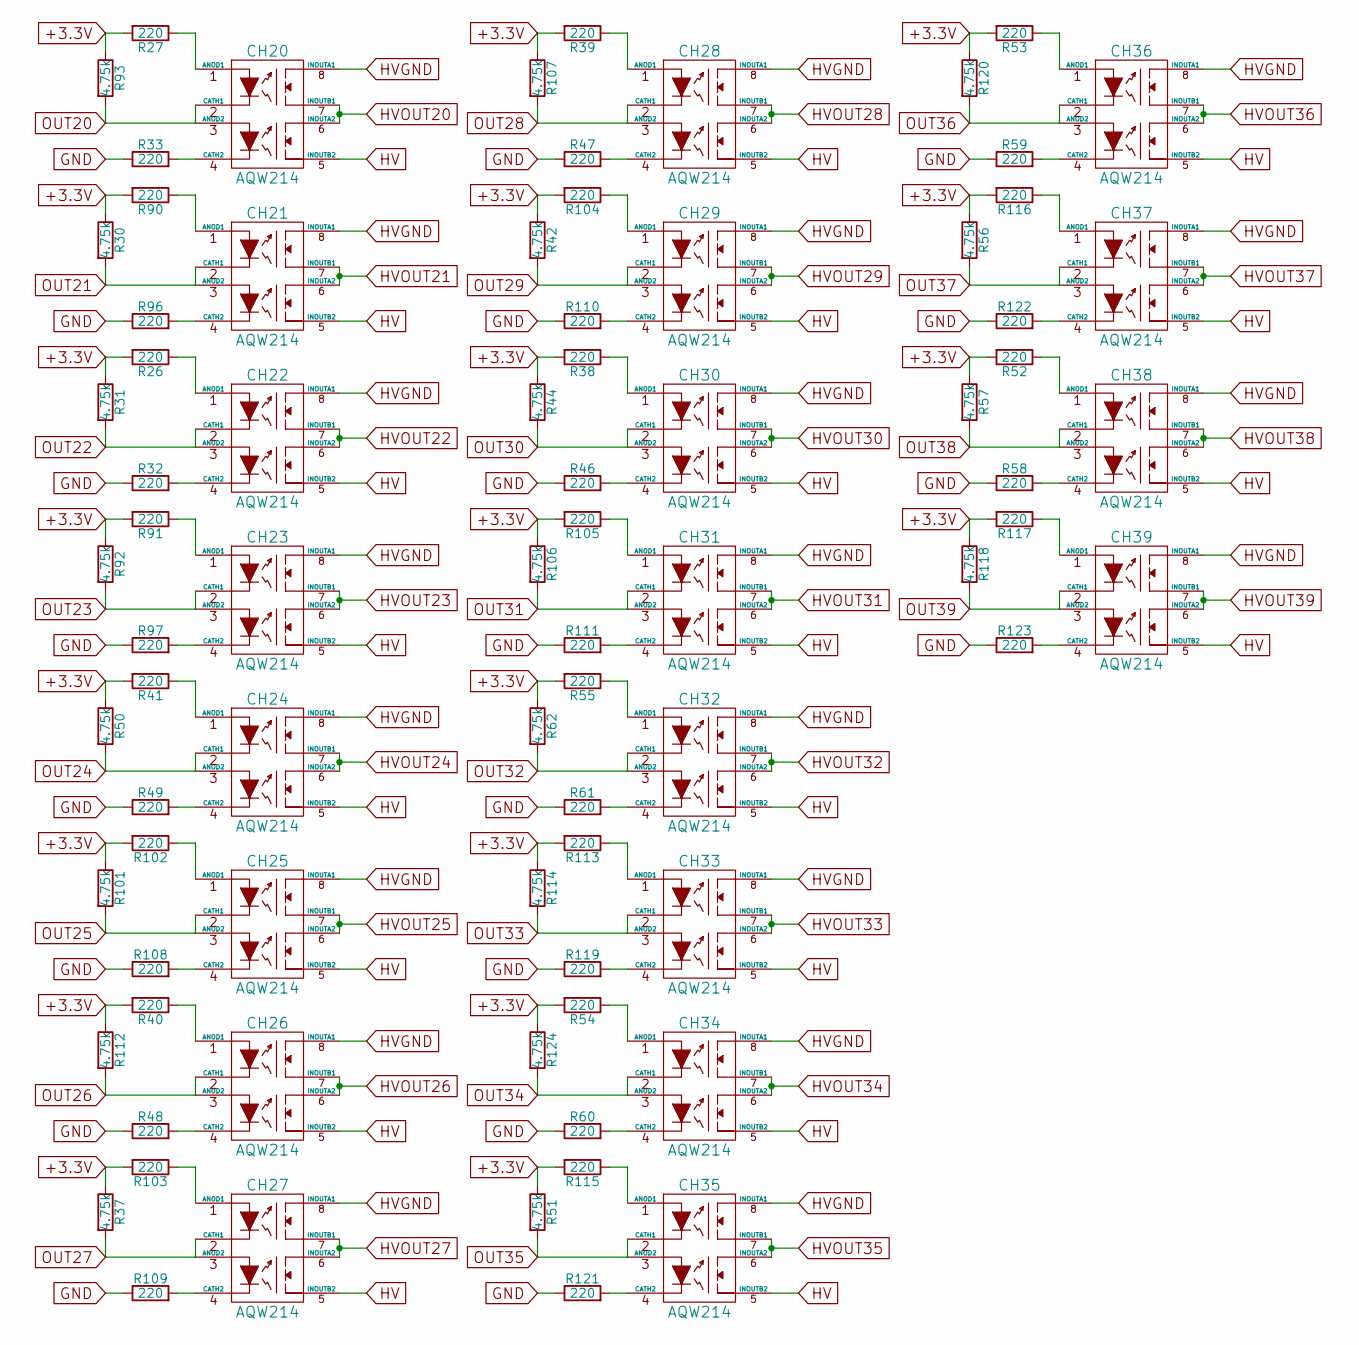
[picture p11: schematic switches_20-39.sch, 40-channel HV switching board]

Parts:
CH20, CH21, CH22, CH23, CH24, CH25, CH26, CH27, CH28, CH29, CH30, CH31, CH32, CH33, CH34, CH35, CH36, CH37, CH38, CH39: AQW214; DIP-8_SMD; MPN AQW214EAZ
R26, R27, R32, R33, R38, R39, R40, R41, R46, R47, R48, R49, R52, R53, R54, R55, R58, R59, R60, R61, R90, R91, R96, R97, R102, R103, R104, R105, R108, R109, R110, R111, R113, R115, R116, R117, R119, R121, R122, R123: 220; R_0805; MPN RC0805FR-07220RL
R30, R31, R37, R42, R44, R50, R51, R56, R57, R62, R92, R93, R101, R106, R107, R112, R114, R118, R120, R124: 4.75k; R_0805; MPN RC0805FR-074K75L

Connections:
+3.3V: R26.2, R27.2, R30.1, R31.1, R37.1, R38.2, R39.2, R40.2, R41.2, R42.1, R44.1, R50.1, R51.1, R52.2, R53.2, R54.2, R55.2, R56.1, R57.1, R62.1, R90.2, R91.2, R92.1, R93.1, R101.1, R102.2, R103.2, R104.2, R105.2, R106.1, R107.1, R112.1, R113.2, R114.1, R115.2, R116.2, R117.2, R118.1, R120.1, R124.1; also elsewhere on the board
GND: R32.1, R33.1, R46.1, R47.1, R48.1, R49.1, R58.1, R59.1, R60.1, R61.1, R96.1, R97.1, R108.1, R109.1, R110.1, R111.1, R119.1, R121.1, R122.1, R123.1; also elsewhere on the board
HV: CH20.5 (INOUTB2), CH21.5 (INOUTB2), CH22.5 (INOUTB2), CH23.5 (INOUTB2), CH24.5 (INOUTB2), CH25.5 (INOUTB2), CH26.5 (INOUTB2), CH27.5 (INOUTB2), CH28.5 (INOUTB2), CH29.5 (INOUTB2), CH30.5 (INOUTB2), CH31.5 (INOUTB2), CH32.5 (INOUTB2), CH33.5 (INOUTB2), CH34.5 (INOUTB2), CH35.5 (INOUTB2), CH36.5 (INOUTB2), CH37.5 (INOUTB2), CH38.5 (INOUTB2), CH39.5 (INOUTB2); also elsewhere on the board
HVGND: CH20.8 (INOUTA1), CH21.8 (INOUTA1), CH22.8 (INOUTA1), CH23.8 (INOUTA1), CH24.8 (INOUTA1), CH25.8 (INOUTA1), CH26.8 (INOUTA1), CH27.8 (INOUTA1), CH28.8 (INOUTA1), CH29.8 (INOUTA1), CH30.8 (INOUTA1), CH31.8 (INOUTA1), CH32.8 (INOUTA1), CH33.8 (INOUTA1), CH34.8 (INOUTA1), CH35.8 (INOUTA1), CH36.8 (INOUTA1), CH37.8 (INOUTA1), CH38.8 (INOUTA1), CH39.8 (INOUTA1); also elsewhere on the board
HVOUT20: CH20.6 (INOUTA2), CH20.7 (INOUTB1); also elsewhere on the board
HVOUT21: CH21.6 (INOUTA2), CH21.7 (INOUTB1); also elsewhere on the board
HVOUT22: CH22.6 (INOUTA2), CH22.7 (INOUTB1); also elsewhere on the board
HVOUT23: CH23.6 (INOUTA2), CH23.7 (INOUTB1); also elsewhere on the board
HVOUT24: CH24.6 (INOUTA2), CH24.7 (INOUTB1); also elsewhere on the board
HVOUT25: CH25.6 (INOUTA2), CH25.7 (INOUTB1); also elsewhere on the board
HVOUT26: CH26.6 (INOUTA2), CH26.7 (INOUTB1); also elsewhere on the board
HVOUT27: CH27.6 (INOUTA2), CH27.7 (INOUTB1); also elsewhere on the board
HVOUT28: CH28.6 (INOUTA2), CH28.7 (INOUTB1); also elsewhere on the board
HVOUT29: CH29.6 (INOUTA2), CH29.7 (INOUTB1); also elsewhere on the board
HVOUT30: CH30.6 (INOUTA2), CH30.7 (INOUTB1); also elsewhere on the board
HVOUT31: CH31.6 (INOUTA2), CH31.7 (INOUTB1); also elsewhere on the board
HVOUT32: CH32.6 (INOUTA2), CH32.7 (INOUTB1); also elsewhere on the board
HVOUT33: CH33.6 (INOUTA2), CH33.7 (INOUTB1); also elsewhere on the board
HVOUT34: CH34.6 (INOUTA2), CH34.7 (INOUTB1); also elsewhere on the board
HVOUT35: CH35.6 (INOUTA2), CH35.7 (INOUTB1); also elsewhere on the board
HVOUT36: CH36.6 (INOUTA2), CH36.7 (INOUTB1); also elsewhere on the board
HVOUT37: CH37.6 (INOUTA2), CH37.7 (INOUTB1); also elsewhere on the board
HVOUT38: CH38.6 (INOUTA2), CH38.7 (INOUTB1); also elsewhere on the board
HVOUT39: CH39.6 (INOUTA2), CH39.7 (INOUTB1); also elsewhere on the board
unnamed: CH20.1 (ANOD1), R27.1
unnamed: CH20.4 (CATH2), R33.2
unnamed: CH21.1 (ANOD1), R90.1
unnamed: CH21.4 (CATH2), R96.2
unnamed: CH22.1 (ANOD1), R26.1
unnamed: CH22.4 (CATH2), R32.2
unnamed: CH23.1 (ANOD1), R91.1
unnamed: CH23.4 (CATH2), R97.2
unnamed: CH24.1 (ANOD1), R41.1
unnamed: CH24.4 (CATH2), R49.2
unnamed: CH25.1 (ANOD1), R102.1
unnamed: CH25.4 (CATH2), R108.2
unnamed: CH26.1 (ANOD1), R40.1
unnamed: CH26.4 (CATH2), R48.2
unnamed: CH27.1 (ANOD1), R103.1
unnamed: CH27.4 (CATH2), R109.2
unnamed: CH28.1 (ANOD1), R39.1
unnamed: CH28.4 (CATH2), R47.2
unnamed: CH29.1 (ANOD1), R104.1
unnamed: CH29.4 (CATH2), R110.2
unnamed: CH30.1 (ANOD1), R38.1
unnamed: CH30.4 (CATH2), R46.2
unnamed: CH31.1 (ANOD1), R105.1
unnamed: CH31.4 (CATH2), R111.2
unnamed: CH32.1 (ANOD1), R55.1
unnamed: CH32.4 (CATH2), R61.2
unnamed: CH33.1 (ANOD1), R113.1
unnamed: CH33.4 (CATH2), R119.2
unnamed: CH34.1 (ANOD1), R54.1
unnamed: CH34.4 (CATH2), R60.2
unnamed: CH35.1 (ANOD1), R115.1
unnamed: CH35.4 (CATH2), R121.2
unnamed: CH36.1 (ANOD1), R53.1
unnamed: CH36.4 (CATH2), R59.2
unnamed: CH37.1 (ANOD1), R116.1
unnamed: CH37.4 (CATH2), R122.2
unnamed: CH38.1 (ANOD1), R52.1
unnamed: CH38.4 (CATH2), R58.2
unnamed: CH39.1 (ANOD1), R117.1
unnamed: CH39.4 (CATH2), R123.2
OUT20: CH20.2 (CATH1), CH20.3 (ANOD2), R93.2; also elsewhere on the board
OUT21: CH21.2 (CATH1), CH21.3 (ANOD2), R30.2; also elsewhere on the board
OUT22: CH22.2 (CATH1), CH22.3 (ANOD2), R31.2; also elsewhere on the board
OUT23: CH23.2 (CATH1), CH23.3 (ANOD2), R92.2; also elsewhere on the board
OUT24: CH24.2 (CATH1), CH24.3 (ANOD2), R50.2; also elsewhere on the board
OUT25: CH25.2 (CATH1), CH25.3 (ANOD2), R101.2; also elsewhere on the board
OUT26: CH26.2 (CATH1), CH26.3 (ANOD2), R112.2; also elsewhere on the board
OUT27: CH27.2 (CATH1), CH27.3 (ANOD2), R37.2; also elsewhere on the board
OUT28: CH28.2 (CATH1), CH28.3 (ANOD2), R107.2; also elsewhere on the board
OUT29: CH29.2 (CATH1), CH29.3 (ANOD2), R42.2; also elsewhere on the board
OUT30: CH30.2 (CATH1), CH30.3 (ANOD2), R44.2; also elsewhere on the board
OUT31: CH31.2 (CATH1), CH31.3 (ANOD2), R106.2; also elsewhere on the board
OUT32: CH32.2 (CATH1), CH32.3 (ANOD2), R62.2; also elsewhere on the board
OUT33: CH33.2 (CATH1), CH33.3 (ANOD2), R114.2; also elsewhere on the board
OUT34: CH34.2 (CATH1), CH34.3 (ANOD2), R124.2; also elsewhere on the board
OUT35: CH35.2 (CATH1), CH35.3 (ANOD2), R51.2; also elsewhere on the board
OUT36: CH36.2 (CATH1), CH36.3 (ANOD2), R120.2; also elsewhere on the board
OUT37: CH37.2 (CATH1), CH37.3 (ANOD2), R56.2; also elsewhere on the board
OUT38: CH38.2 (CATH1), CH38.3 (ANOD2), R57.2; also elsewhere on the board
OUT39: CH39.2 (CATH1), CH39.3 (ANOD2), R118.2; also elsewhere on the board

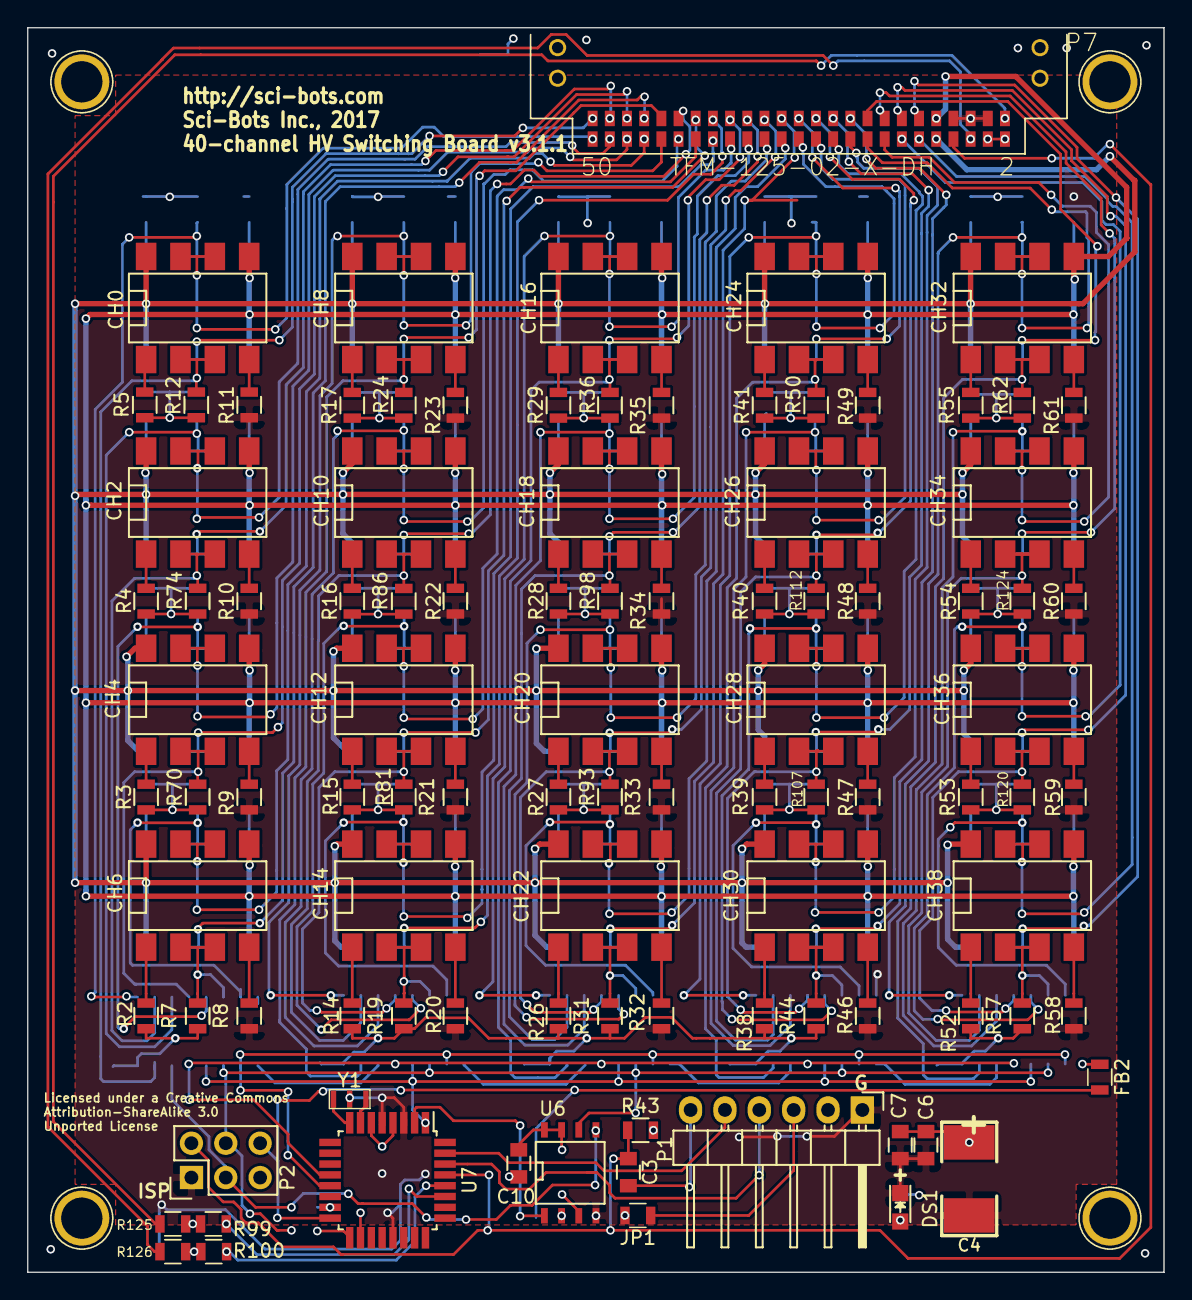
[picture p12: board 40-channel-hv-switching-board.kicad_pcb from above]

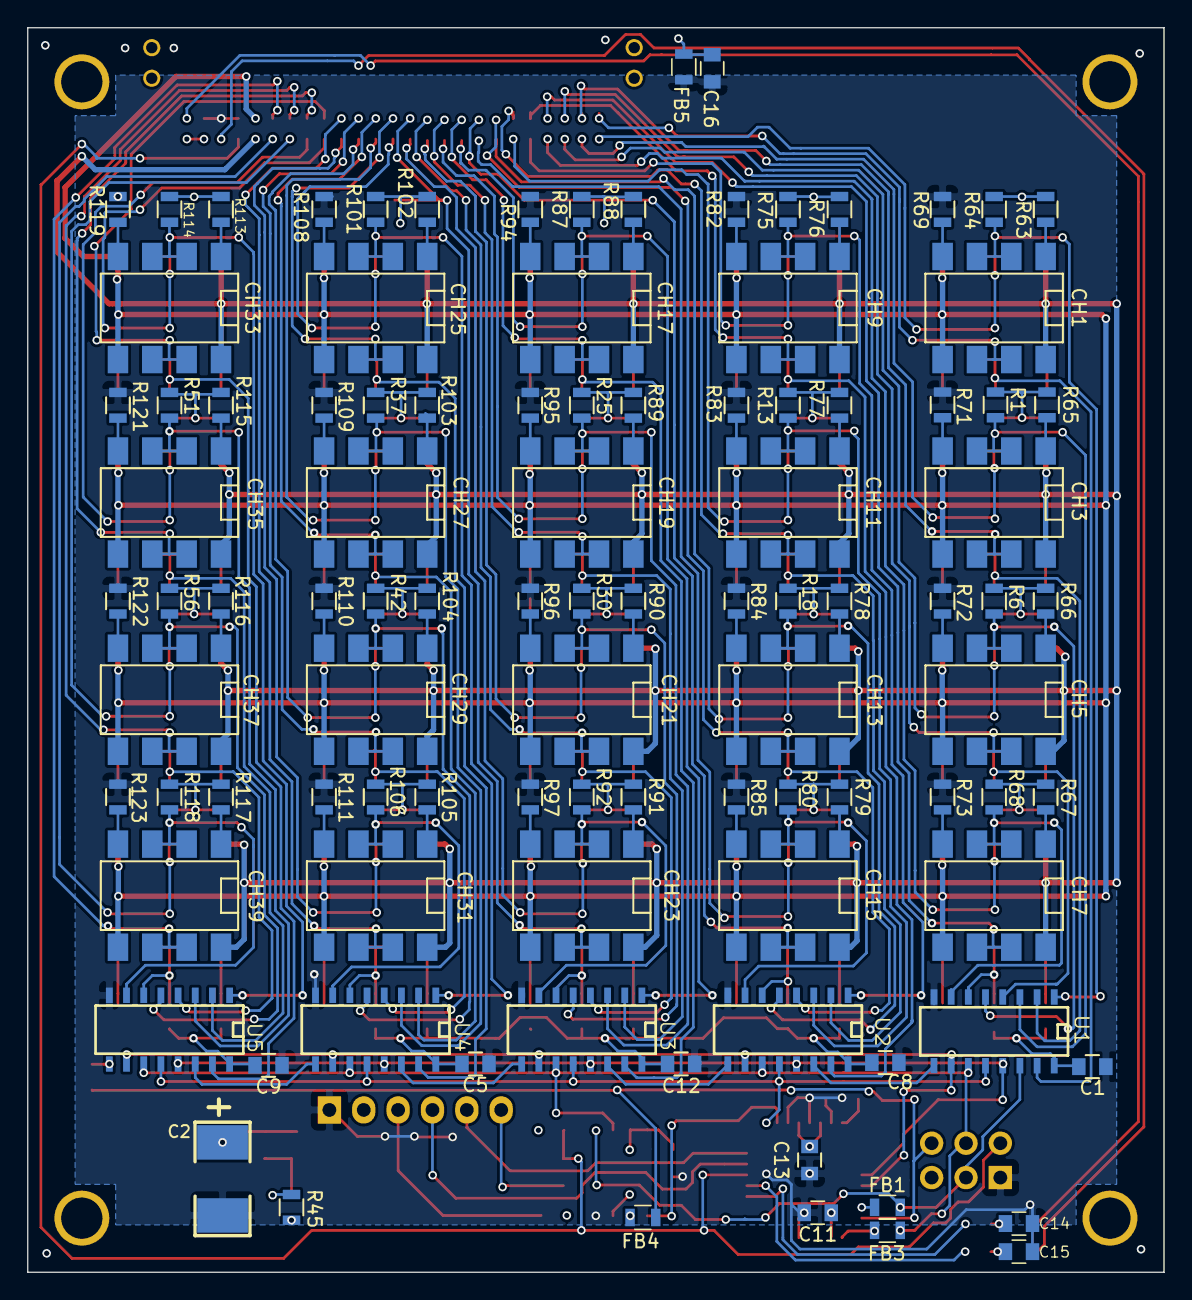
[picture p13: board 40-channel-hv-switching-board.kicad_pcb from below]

Board: 4 copper layers, 84.0 x 92.0 mm, 204 parts (101 on the bottom side), 194 nets.

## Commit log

2011-08-02 Version 1.0 (sent for fabrication on 08/01/2011)
    [40-channel HV switching board-BOM.xls, 40-channel HV switching board-p1.sch, 40-channel HV switching board-p2.sch, 40-channel HV switching board-p3.sch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]
2011-11-18 Fix capcitor values on schematic, swap HV/GND on BNC jacks
    [40-channel HV switching board-p1.sch, 40-channel HV switching board-p2.sch, 40-channel HV switching board-p3.sch, 40-channel HV switching board-p4.sch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]
2012-02-22 [SUBMODULE] add wheelerlab kicad library as submodule
    [40-channel HV switching board-Back.gbl, 40-channel HV switching board-Front.gtl, 40-channel HV switching board-Ground_plane.gbr, 40-channel HV switching board-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]
2012-03-16 Update BOM for PCB assembly
    [40-channel HV switching board-BOM.xls, 40-channel HV switching board-p1.sch, 40-channel HV switching board-p2.sch, 40-channel HV switching board-p3.sch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]
2012-03-16 Add cost estimates to BOM
    [40-channel HV switching board-BOM.xls]
2012-04-27 Fix HV/GND connection on BNC
    Commit fdaa8f8 only fixed the schematic, not the brd file.
    [40-channel HV switching board-Back.gbl, 40-channel HV switching board-Front.gtl, 40-channel HV switching board-Ground_plane.gbr, 40-channel HV switching board-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]
2013-01-18 Reindex channels to start at 0 instead of 1
    This makes the hardware/software channel labels consistent.
    [40-channel HV switching board-BOM.xls, 40-channel HV switching board-p1.sch, 40-channel HV switching board-p2.sch, 40-channel HV switching board-p3.sch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]
2013-01-18 Replace 50-channel IDE connector with 40-channel
    [40-channel HV switching board-p1.sch, 40-channel HV switching board-p2.sch, 40-channel HV switching board-p3.sch, 40-channel HV switching board-p4.sch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]
2013-01-19 Remove HV plane and make board smaller
    [40-channel HV switching board.brd]
2013-05-09 Use molex connector, fix BOM, ground planes, add logo
    [40-channel HV switching board-BOM.xls, 40-channel HV switching board-B_Mask.gbs, 40-channel HV switching board-B_SilkS.gbo, 40-channel HV switching board-Back.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]
2013-08-16 Swap BNC connectors for SMA, make board wider, add mounting holes
    [40-channel HV switching board-BOM.xls, 40-channel HV switching board-B_Mask.gbs, 40-channel HV switching board-B_SilkS.gbo, 40-channel HV switching board-Back.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]
2013-09-11 Update library, add paste and pos gerber files
    [40-channel HV switching board-B_Paste.gbp, 40-channel HV switching board-F_Paste.gtp, 40-channel HV switching board-p1.sch, 40-channel HV switching board-p2.sc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]
2014-01-28 Reroute onto 2-layer board, remove inverters
    [40-channel HV switching board-BOM.xls, 40-channel HV switching board-B_Mask.gbs, 40-channel HV switching board-B_Paste.gbp, 40-channel HV switching board-B_Sil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]
2014-02-12 Reduce board footprint and replace GPIO
    * Add ATMega328 chip and 74HC595s instead of GPIO
    * Add jumpers to power MCU from USB and relays from VCC instead of PSU
    * Com. bus should be capable of running at 5V or 3.3V
    [40-channel HV switching board-BOM.xls, 40-channel HV switching board-B_Mask.gbs, 40-channel HV switching board-B_Paste.gbp, 40-channel HV switching board-B_Sil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]
2014-04-24 Fix polarity label on C4
    [40-channel HV switching board.kicad_pcb]
2014-04-30 Rename PhotoMOS reference numbers to match channel number
    [40-channel HV switching board-BOM.xls, 40-channel HV switching board-B_Mask.gbs, 40-channel HV switching board-B_Paste.gbp, 40-channel HV switching board-B_Sil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]
2014-04-30 Add ISP latch circuit, use soft SPI
    * replace 0603 caps with 1206
    * label jumpers
    * add LEDs for VCC, 5V, PROG MODE, and RESET
    * move serial header to make it more accessible
    [40-channel HV switching board-B_Mask.gbs, 40-channel HV switching board-B_Paste.gbp, 40-channel HV switching board-B_SilkS.gbo, 40-channel HV switching board-B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]
2014-05-05 Modify ISP latch circuit, fix BOM
    * Use 74LV00 NAND gate for ISP latch (3.3V compatible)
    [40-channel HV switching board-BOM.xls, 40-channel HV switching board-B_Mask.gbs, 40-channel HV switching board-B_Paste.gbp, 40-channel HV switching board-B_Sil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]
2014-05-05 Make LED current-limiting resistors 1k
    [40-channel HV switching board-BOM.xls, 40-channel HV switching board-p1.sch, 40-channel HV switching board.kicad_pcb]
2014-05-08 Add decoupling capacitor to 7400 chip, label LED polarity
    [40-channel HV switching board-BOM.xls, 40-channel HV switching board-B_Mask.gbs, 40-channel HV switching board-B_Paste.gbp, 40-channel HV switching board-B_Sil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]
2014-05-28 Fix BOM, labels, reorganize schematic
    [40-channel HV switching board-BOM.csv, 40-channel HV switching board-BOM.xls, 40-channel HV switching board-B_Mask.gbs, 40-channel HV switching board-B_Paste.g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]
2014-06-11 Fix part number on BOM for P1
    [40-channel HV switching board-BOM.csv]
2014-07-16 Replace wrong SMA jack on BOM
    [40-channel HV switching board-BOM.csv]
2014-07-24 Put BOM in format for gold phoenix
    [40-channel HV switching board-BOM.csv]
2015-08-26 Fix quantity of 1kOhm resistors (5 instead of 4)
    [40-channel HV switching board-BOM.csv]
2016-02-09 Update for compatibility with KiCad 4.0
    [40-channel HV switching board.sch, switches_0-19.sch, switches_20-39.sch]
2016-02-09 Fix footprint for C2 and C4 in BOM
    [40-channel HV switching board-BOM.csv]
2016-09-27 Update to work with KiCad 4.0
    [40-channel HV switching board-B.Mask.gbs, 40-channel HV switching board-B.Paste.gbp, 40-channel HV switching board-B.SilkS.gbo, 40-channel HV switching board-B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]
2016-09-27 [WIP] Switch caps and LEDs to 0805 footprints
    [40-channel HV switching board-BOM.csv, 40-channel HV switching board.kicad_pcb, 40-channel HV switching board.sch]
2016-09-28 [WIP] Add sci-bots logo
    [40-channel HV switching board-B.Mask.gbs, 40-channel HV switching board-B.Paste.gbp, 40-channel HV switching board-B.SilkS.gbo, 40-channel HV switching board-B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]
2016-09-28 [WIP] Fix placement of crystal, bump version to 2.1.1
    [40-channel HV switching board-B.Mask.gbs, 40-channel HV switching board-B.Paste.gbp, 40-channel HV switching board-B.SilkS.gbo, 40-channel HV switching board-B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]
2016-12-01 Use edge connector, 3.3V logic, smaller board, etc.
    [40-channel HV switching board-B.Mask.gbs, 40-channel HV switching board-B.Paste.gbp, 40-channel HV switching board-B.SilkS.gbo, 40-channel HV switching board-B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]
2016-12-06 Breakout reset pin to edge connector
    [40-channel HV switching board-B.Mask.gbs, 40-channel HV switching board-B.Paste.gbp, 40-channel HV switching board-B.SilkS.gbo, 40-channel HV switching board-B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]
2016-12-19 Add SPI flash memory, move edge connector to side
    [40-channel HV switching board-B.Mask.gbs, 40-channel HV switching board-B.Paste.gbp, 40-channel HV switching board-B.SilkS.gbo, 40-channel HV switching board-B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]
2017-01-05 Update BOM
    [40-channel HV switching board-BOM.csv, 40-channel HV switching board.sch, 40-channel HV switching board_BOM.csv, switches_0-19.sch]
2017-02-09 Remove schematic cache library
    [40-channel HV switching board.sch, switches_0-19.sch, switches_20-39.sch]
2017-03-01 [WIP] Improved layout for EMC
    * ground mounting holes
    * Add 3.3V and GND power planes
    * use solder jumper instead of header pins
    * replace edge connector
    * extend length of board
    * move programming header so that it doesn't extend past the edge of the board
    [40-channel HV switching board.kicad_pcb, 40-channel HV switching board.sch, switches_0-19.sch, switches_20-39.sch]
2017-03-07 Lots of fixes to prepare for EMC testing
    * read output of shift registers
    * fix flash chip connection
    * replace jumpers with 0805 pads
    * reduce length to 92mm
    * filter i2c lines
    * protect i2c lines
    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
    [40-channel HV switching board-B.Mask.gbs, 40-channel HV switching board-B.Paste.gbp, 40-channel HV switching board-B.SilkS.gbo, 40-channel HV switching board-B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]
2017-04-05 Fix BOM, version number on schematics
    [40-channel HV switching board.sch, 40-channel HV switching board_BOM.csv, switches_0-19.sch, switches_20-39.sch]
2017-04-05 Update part numbers for i2c filters
    [40-channel HV switching board-B.Mask.gbs, 40-channel HV switching board-B.Paste.gbp, 40-channel HV switching board-B.SilkS.gbo, 40-channel HV switching board-B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]
2017-06-02 Change resistor values use standard ref prefixes
    * Fix #1 and #2
    [40-channel HV switching board-B.Mask.gbs, 40-channel HV switching board-B.Paste.gbp, 40-channel HV switching board-B.SilkS.gbo, 40-channel HV switching board-B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]
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2021-11-17 Fix broken symbols
    [40-channel-hv-switching-board.sch, switches_0-19.sch, switches_20-39.sch]
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2021-11-22 Fix schematic power flags (broken by git filter)
    [40-channel-hv-switching-board.sch]
2021-11-24 Fix BOM
    [40-channel-hv-switching-board-BOM.csv, switches_0-19.sch, switches_20-39.sch]
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

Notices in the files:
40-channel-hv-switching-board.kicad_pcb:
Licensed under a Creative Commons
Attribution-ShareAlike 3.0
